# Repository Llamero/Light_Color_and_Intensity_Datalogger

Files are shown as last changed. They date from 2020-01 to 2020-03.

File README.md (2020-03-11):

# Data Logger: Temperature, Pressure, Humidity, Light Intensity and Color

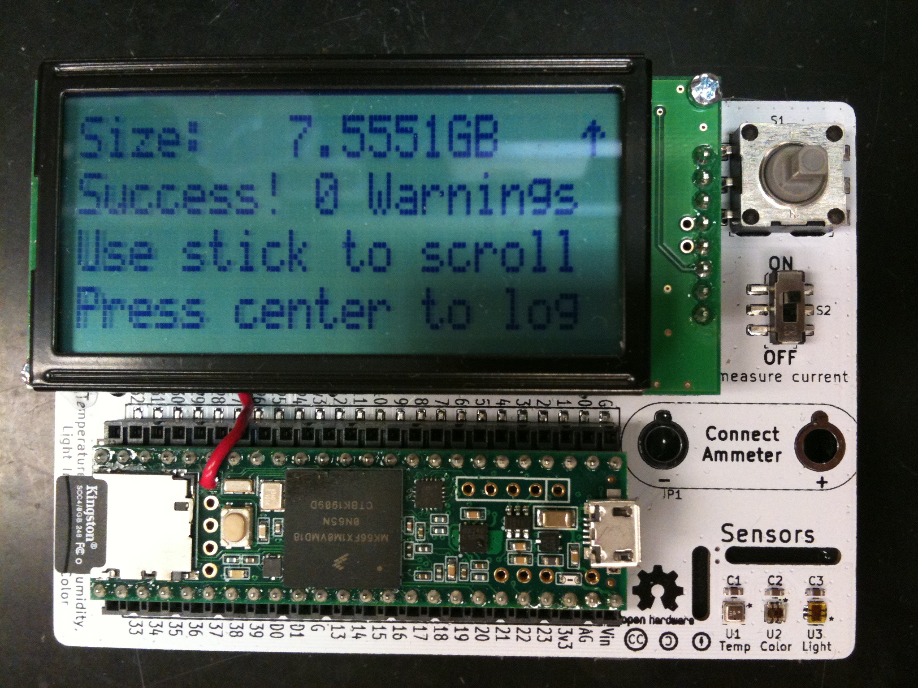
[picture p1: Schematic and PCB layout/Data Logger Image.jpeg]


## Summary:

This is an open-source data logger that can record air temperature, air pressure, relative humidity, visible light instensity, near-infrared light intensity, and visible light color (RGB).  This data logger can record at up to 1 Hz onto a FAT32 formatted SD card.  At 1Hz and with a full battery pack (6 AAs) the data logger should run for 200+ days on a single pack (depending on the SD card), with lower sampling frequencies increasing the duration to a maximum of >800 days (depending on the SD card).  The light sensors employ an autogain feature with the intensity sensor having a 600,000,000:1 dynamic range, and a minimum sensitivity at about 1.0 nW/cm2.

Windows users: Use this program to format SD cards >32 GB http://www.ridgecrop.demon.co.uk/index.htm?guiformat.htm

For information on ordering, assembly, and programming, please see the instruction manual. 

Development of this data logger was funded by NIH P30-EY003176-32

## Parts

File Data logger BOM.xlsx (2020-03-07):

Part ID | Value | Footprint | Manufacturer | Manufacturer Part # | Digikey Part # | Quantity | Link
BT1 | BU2032SM-BT-GTR | Ben_Custom:BU2032SM-BT-GTR | MPD (Memory Protection Devices) | BU2032SM-BT-GTR | BU2032SM-BT-GCT-ND | 1 | https://www.digikey.com/product-detail/en/mpd-memory-protection-devices/BU2032SM-BT-GTR/BU2032SM-BT-GCT-ND/3628531
BT2, BT3 | Battery | Ben_Custom:BH3AAW-Battery_wire_pads | MPD (Memory Protection Devices) | SBH331A | SBH331A-ND | 2 | https://www.digikey.com/products/en?keywords=SBH331A-ND
C1-C3 | 1uF | Capacitors_SMD:C_0603 | TDK Corporation | C1608X7R1C105K080AC | 445-1604-1-ND | 3 | https://www.digikey.com/products/en?keywords=445-1604-1-ND
C4 | 100uF | Capacitors_SMD:C_1206 | Samsung Electro-Mechanics | CL31A107MQHNNNE | 1276-1782-1-ND | 1 | https://www.digikey.com/products/en?keywords=1276-1782-1-ND
D1-D2 | D | Diodes_SMD:D_SOD-323 | Toshiba Semiconductor and Storage | CUS10S30,H3F | CUS10S30H3FCT-ND | 2 | https://www.digikey.com/products/en?keywords=CUS10S30H3FCT-ND
LCD1 | NHD-0420H1Z-FL-GBW-33V3 | Ben_Custom:NHD-0420H1Z-FL-GBW-33V3_Display_with_Header | Newhaven Display Intl | NHD-0420H1Z-FL-GBW-33V3 | NHD-0420H1Z-FL-GBW-33V3-ND | 1 | https://www.digikey.com/products/en?keywords=NHD-0420H1Z-FL-GBW-33V3
LCD Header | SSM-108-L-SV-BE-LC | Ben_Custom:NHD-0420H1Z-FL-GBW-33V3_Display_with_Header | Samtec Inc. | SSM-108-L-SV-BE-LC | SSM-108-L-SV-BE-LC-ND | 2 | https://www.digikey.com/products/en?keywords=SSM-108-L-SV-BE-LC-ND
LCD Standoff | 970100244 | Ben_Custom:NHD-0420H1Z-FL-GBW-33V3_Display_with_Header | Würth Elektronik | 970100244 | 732-12845-ND | 2 | https://www.digikey.com/products/en?keywords=732-12845-ND
LCD Bolt | MPMS 002 0005 PH | Ben_Custom:NHD-0420H1Z-FL-GBW-33V3_Display_with_Header | B&F Fastener Supply | MPMS 002 0005 PH | H738-ND | 100 | https://www.digikey.com/products/en/hardware-fasteners-accessories/screws-bolts/572?k=H738-ND
Q1 | Q_NMOS_GSD | TO_SOT_Packages_SMD:SOT-23 | Infineon Technologies | BSS806NH6327XTSA1 | BSS806NH6327XTSA1CT-ND | 1 | https://www.digikey.com/products/en?keywords=BSS806NH6327XTSA1CT-ND
R1 | EXB-2HV472JV_-_8x4.7k_resistor_array | Ben_Custom:4816P-1-472LF | Bourns Inc. | 4816P-1-472LF | 4816P-1-472LFCT-ND | 1 | https://www.digikey.com/products/en?keywords=4816P-1-472LFCT-ND
R2 | 2 Ohm | Resistors_SMD:R_0603 | Yageo | RC0603FR-072RL | 311-2.00HRCT-ND | 1 | https://www.digikey.com/products/en?keywords=311-2.00HRCT-ND
S1 | JS5208 | digikey-footprints:Switch_Nav_12.4x12.4mm_SMD_JS5208 | E-Switch | JS5208 | EG4561-ND | 1 | https://www.digikey.com/products/en?keywords=EG4561-ND
S2 | JS202011SCQN | digikey-footprints:Switch_Slide_JS202011SCQN | C&K | JS202011SCQN | 401-2002-1-ND | 1 | https://www.digikey.com/products/en?keywords=401-2002-1-ND
U1 | BME280 | digikey-footprints:Pressure_Sensor_LGA-8_2.5x2.5mm_BME280 | Bosch Sensortec | BME280 | 828-1063-1-ND | 1 | https://www.digikey.com/products/en?keywords=828-1063-1-ND
U2 | TCS34725FN | Ben_Custom:TCS34725 | ams | TCS34725FN | TCS34725FNCT-ND | 1 | https://www.digikey.com/products/en?keywords=TCS34725FNCT-ND
U3 | TSL25911FN | Ben_Custom:TSL25911FN | ams | TSL25911FN | TSL25911FNCT-ND | 1 | https://www.digikey.com/products/en?keywords=TSL25911FNCT-ND
U4 | Teensy3.6 | Ben_Custom:Teensy3.6_doublewide_header | SparkFun Electronics | DEV-14058 | 1568-1465-ND | 1 | https://www.digikey.com/products/en?keywords=1568-1465-ND
U5 | TS12A4514DBVR | TO_SOT_Packages_SMD:SOT-23-5 |  | TS12A4514DBVR | 296-24201-1-ND | 1 | https://www.digikey.com/products/en?keywords=296-24201-1-ND
Teensy Header | SSM-124-L-DV-LC | Ben_Custom:Teensy3.6_doublewide_header | Samtec Inc. | SSM-124-L-DV-LC | SSM-124-L-DV-LC-ND | 2 | https://www.digikey.com/products/en?keywords=SSM-124-L-DV-LC-ND
# of decives: | 1

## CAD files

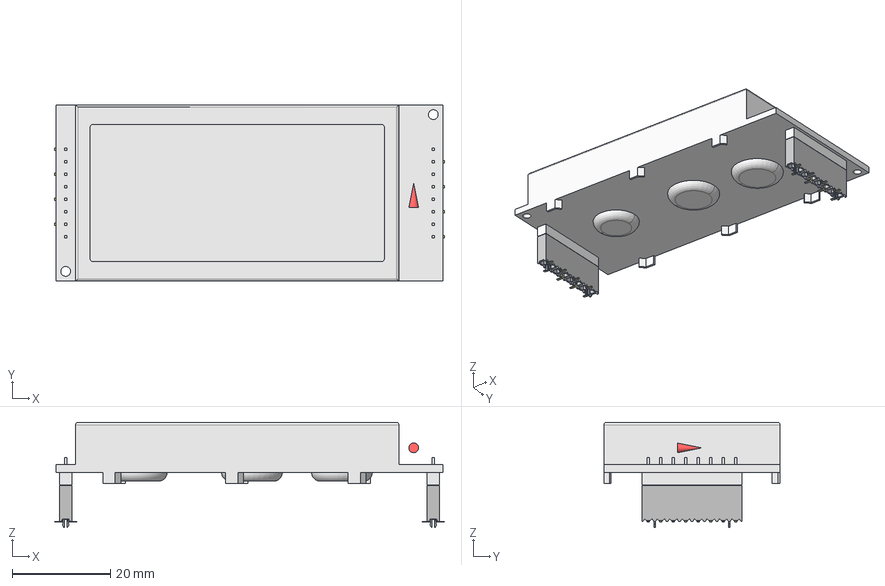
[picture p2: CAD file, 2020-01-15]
Schematic and PCB layout/Light_intensity_data_logger/CAD files/Display with header.FCStd
79.6 x 36.0 x 21.5 mm
NHD_0420H1Z
_SSM-108-L-SV-BE-LC_body
_C-95-028
_SSM-108-L-SV-BE-LC_body001
_C-95-029

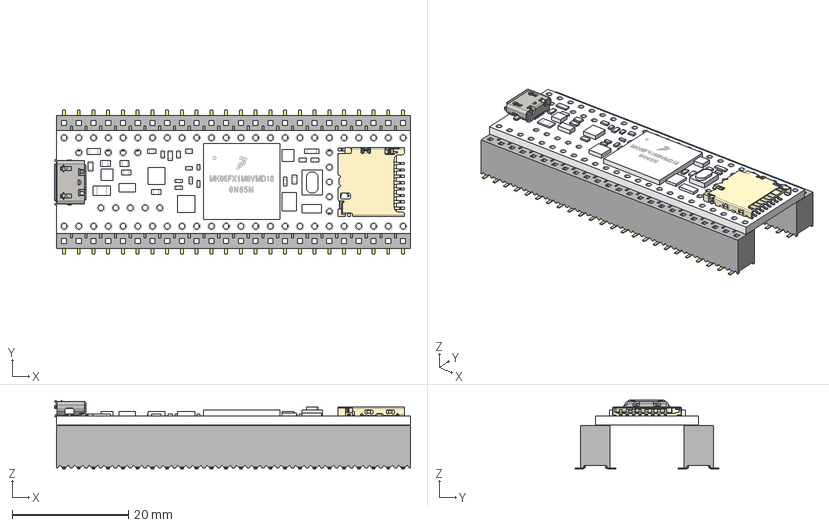
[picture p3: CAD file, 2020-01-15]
Schematic and PCB layout/Light_intensity_data_logger/CAD files/Teensy 35_36 on doublewide header.FCStd
61.3 x 24.8 x 11.8 mm
Teensy 3_5
DM3D-SF
_SSM-124-T-DV_body
_C-137-0124
_SSM-124-T-DV_body001
_C-137-0125

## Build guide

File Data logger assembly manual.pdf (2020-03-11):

# Data logger Manual

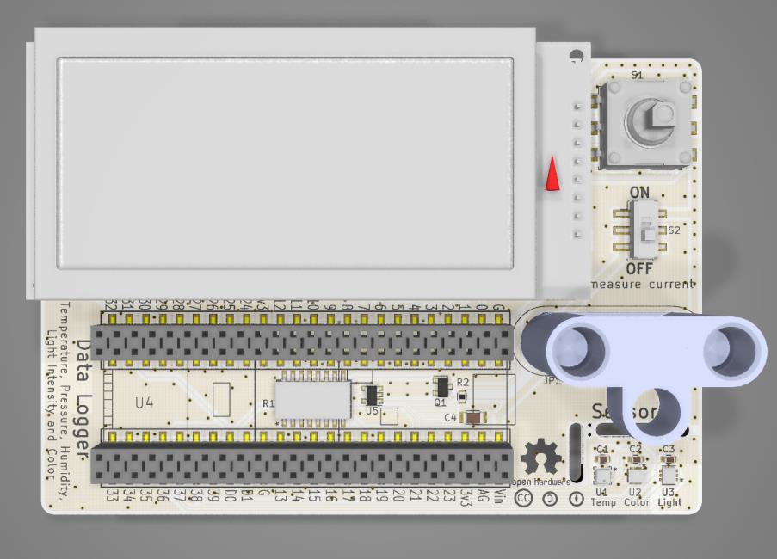
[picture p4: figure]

# Board ordering

To build the data logger, you will need a PCB board. To greatly ease assembly, you will also want a solder paste stencil. Both of these can be easily ordered by submitting the Gerber files to a PCB and stencil fabricator. Several such vendors include Aisler, PCBWay, JLCPCB, etc.

Board specifications:

Size: 69 x 100 mm

Board: 1.6 mm FR4

Copper : 1 oz/ft²

Surface finish: HASL with lead or ENIG

Vias: Tented

Stencil specifications:

Type: Non-framework (unless you have a stencil printer: http://www.madelltech.com/m2-4.html)

Electropolishing: Yes (this is essential to prevent the solder paste from sticking onto the stencil)

# Parts ordering

Parts can be easily ordered by submitting the bill-of-materials (Data logger BOM.xlsx) (https://github.com/Llamero/Light_Color_and_Intensity_Datalogger/blob/master/Data%20logger%20BOM.xlsx) to any major parts vendor including Digikey (https://www.digikey.com/bom) or Mouser (https://www.mouser.com/bom/). The BOM is setup to automatically calculate the number of parts needed based on the number of boards specified.

# Equipment needed:

Tape

Single edge razor blade

Disposable stirrer (pipette tips work well)

Soldering iron

Solder

Solder paste

Solder flux

Magnifying glass or microscope

Tweezers or forceps

Thermometer

Hot plate

Hot glue gun

Aluminum foil

Disposable latex or nitrile gloves

70% Ethanol or rubbing alcohol

Optional: Container for pre-sorting components

# Soldering the board

Before starting with assembly of the board be sure to read and understand all of the following instructions. Once the solder paste is applied the board must be reflowed within two hours or too much of the flux will evaporate. Also be sure to change your gloves regularly during the application of the solder paste. Solder paste can readily get into the skin, posing a health hazard. Hazards aside, assembling a PCB board is very much akin to building a model or advanced Lego® kit with no advanced skills required. Here is an additional tutorial on solder paste stenciling (https://www.sparkfun.com/tutorials/58) and reflow (https://www.sparkfun.com/tutorials/59).

### Step 1: Tape PCB boards together

You want to tape the board to another PCB board so that the stencil can be attached to a flat surface.

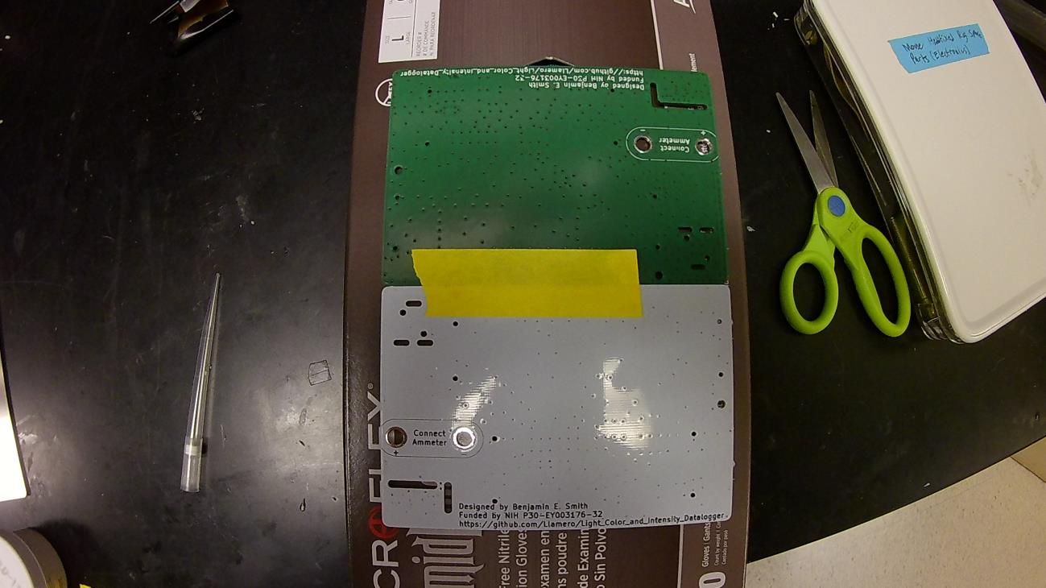
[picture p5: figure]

### Step 2: Align stencil onto PCB

Using a microscope or magnifying glass, try to align the stencil as accurately as possible with all of the stencil holes lining up with all of the PCB pads. Small errors (less than half a pad spacing) are tolerable as the solder will wick to the correct position, but the more aligned the better. The sensor pads are the most closely spaced, so be extra careful to align them properly.

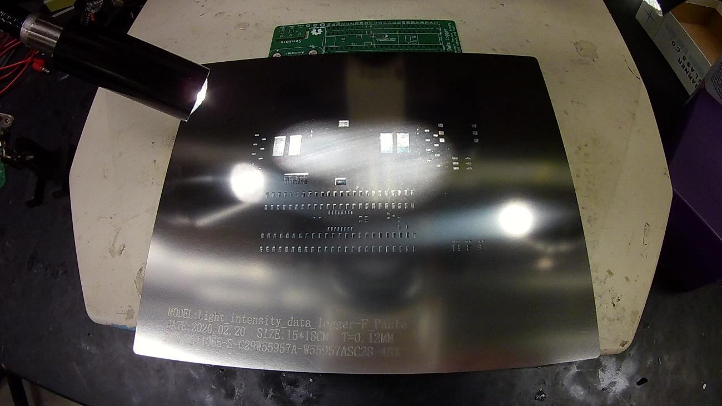
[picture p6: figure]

### Step 3: Tape stencil in place onto spare PCB

Carefully tape the stencil into place, and then press down the on the stencil to check the alignment. Repeat steps 2-3 if the stencil looks off center.

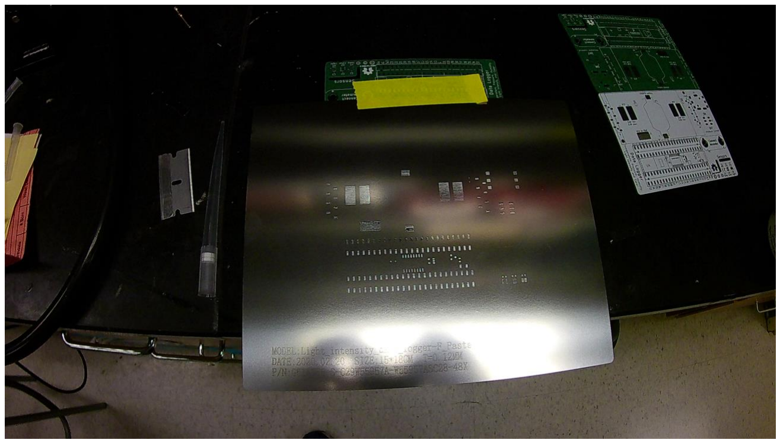
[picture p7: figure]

### Step 4: Thoroughly mix the solder paste

Put on a pair of disposable gloves and vigorously mix the solder paste with a disposable stirrer (such as a pipette tip) for at least one minute. Inadequately mixed solder paste can lead to poor solder reflow.

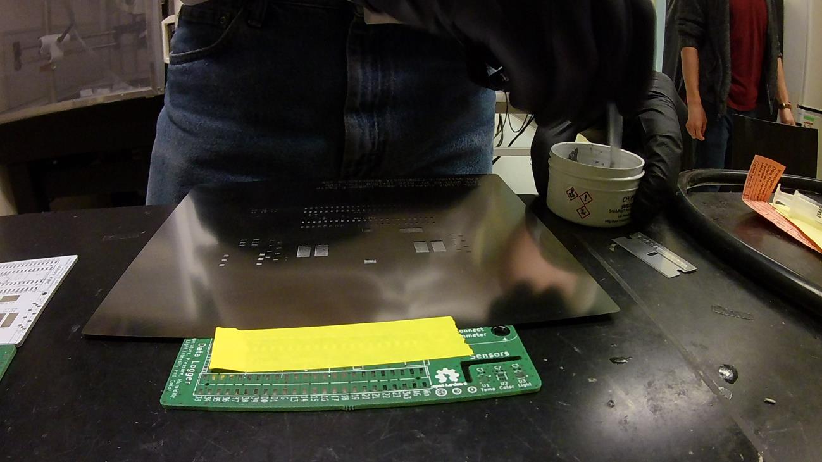
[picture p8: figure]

### Step 5: Apply solder paste to the razor blade

Using the stirrer to apply a generous amount of solder paste to the blade edge of the razor blade.

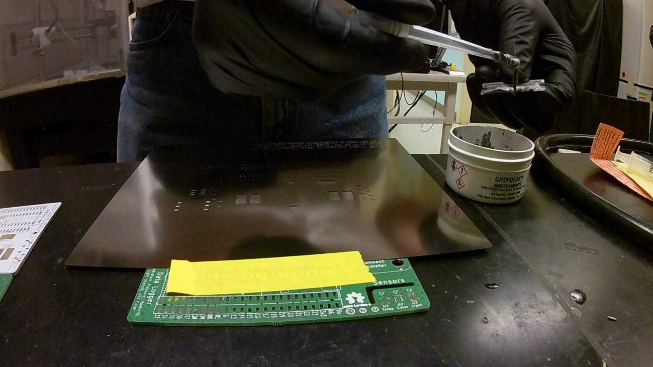
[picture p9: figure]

### Step 6: Apply thick layer of solder paste to the stencil

Use the razor blade to apply a coat of solder paste to the stencil, ensuring you cover all of the pads. Try to move across the stencil at a 45° angle to reduce the risk of pressing paste under the stencil. It will likely take multiple applications to cover the entire stencil.

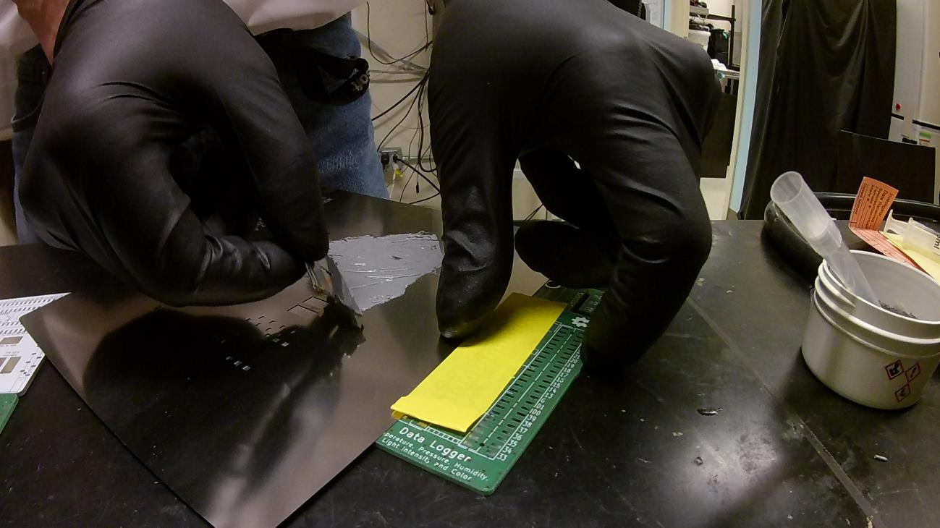
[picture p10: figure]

### Step 7: Remove all excess solder paste

Press the razor blade onto the stencil and carefully scrape off all of the excess solder paste. Use the stirrer to remove the excess paste from the blade and return it to the solder paste container.

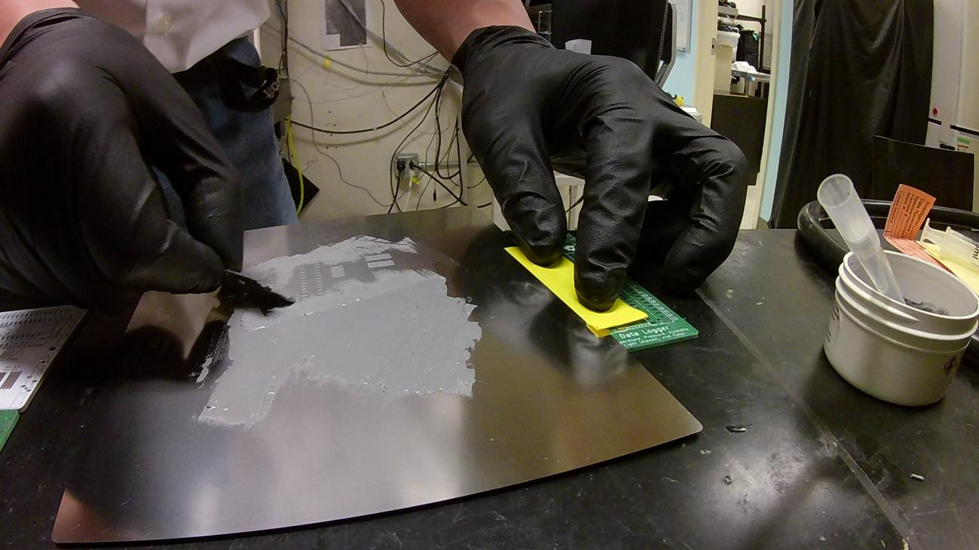
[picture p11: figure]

### Step 8: Lift the stencil from the PCB board

Once all of the excess paste is removed from the stencil, lift the stencil from the PCB by pulling up on the side opposite the tape. Once the stencil is clear of the PCB, carefully remove the tape from the stencil and PCB, and remove the spare PCB the stencil was attached to. Inspect the PCB to make sure all the pads are covered in solder paste, and then properly dispose of the blade and stirrer, and clean the stencil thoroughly with 70% ethanol or rubbing alcohol. Also return the solder paste to 4°C storage.

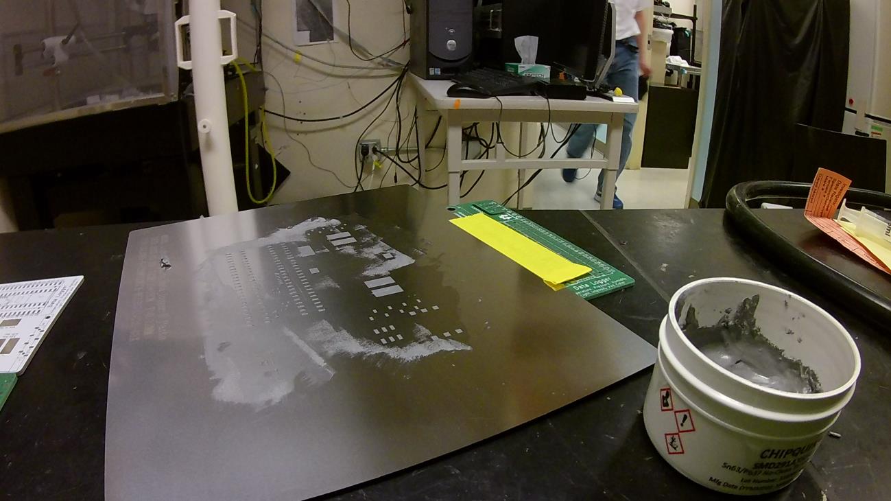
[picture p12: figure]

### Step 9: Add components to the PCB board

Using forceps, carefully place each component onto the board. All components should have a numerical identifier on the BOM (such as “R1”) that corresponds to a marking on the board. Chips that have a specific orientation will have a dot next to pin #1, and there is as asterisk next to the corresponding pad on the PCB. Diodes should be aligned such that the line on the diode goes into the U shaped mark on the PCB: The light sensors are an exception since the epoxy cover is clear. For these chips, pin #1 is marked by a pad that is thinner than the other pads (see picture below – the green arrow points to the pin #1 pad which is thinner than the other three corner pads – magenta arrows). Do not add the joystick (S1) as this will be hand soldered on later.

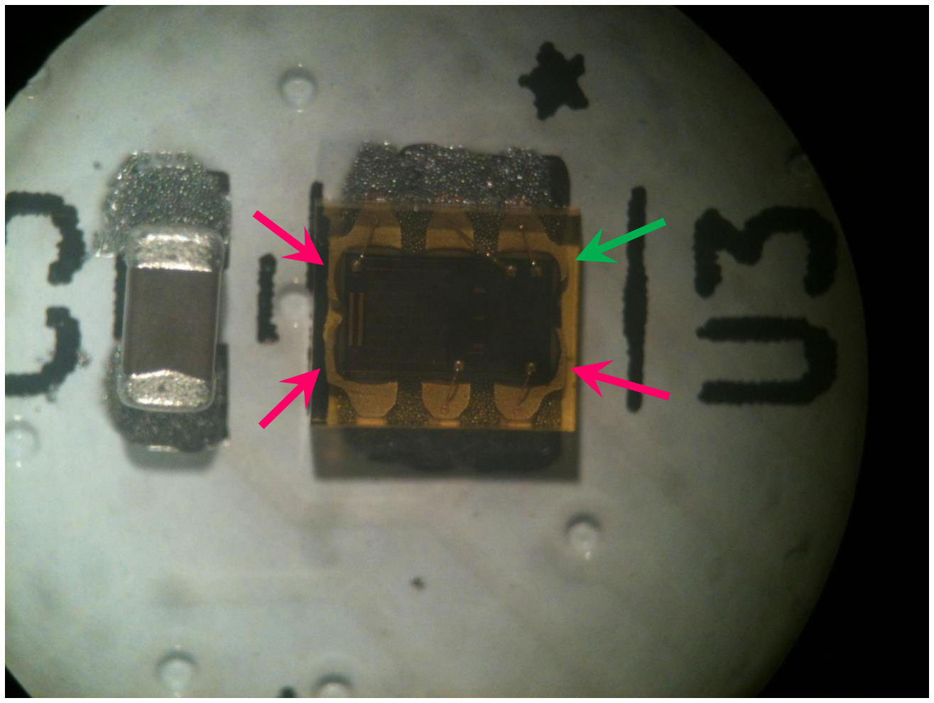
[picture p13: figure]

### Step 10: Reflow the board

Once all of the parts are placed, double check all the components to make sure they are oriented properly, then transfer the board onto a piece of aluminum foil, and place the boards onto a hot plate. Make sure the hot plate is near a fume hood or is in a well ventilated area, as the flux will fume as it burns off. Turn on the heat to the hot plate and monitor the temperature with the thermometer. If you are using lead solder paste, the solder should melt at 183°C. Continue heating the board to around 220°C, and make sure that all of the solder has melted. Since the solder is under the sensors, you can gently tap the sensor chips with a pair of forceps. If they snap back, the solder has melted. Carefully lift the aluminum foil with the boards off of the hot plate, and allow them to cool.

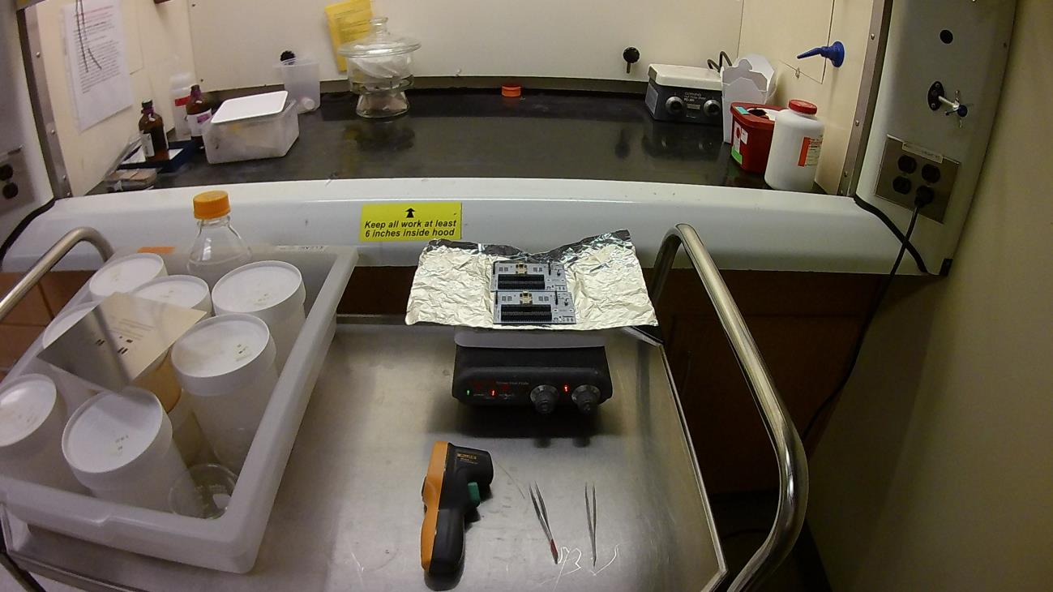
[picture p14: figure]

### Step 11: Inspect the board

Once the boards have cooled, inspect all of the solder joints to make sure they reflowed properly. All joints should look shiny. If you see dull joints, these have not fully reflowed, so apply a small amount of flux to the joint and melt it with a soldering iron. Solder bridges (two or more pins soldered together) can be easily removed by applying a small amount of flux to the bridge, and then tapping the bridge with a clean soldering iron.

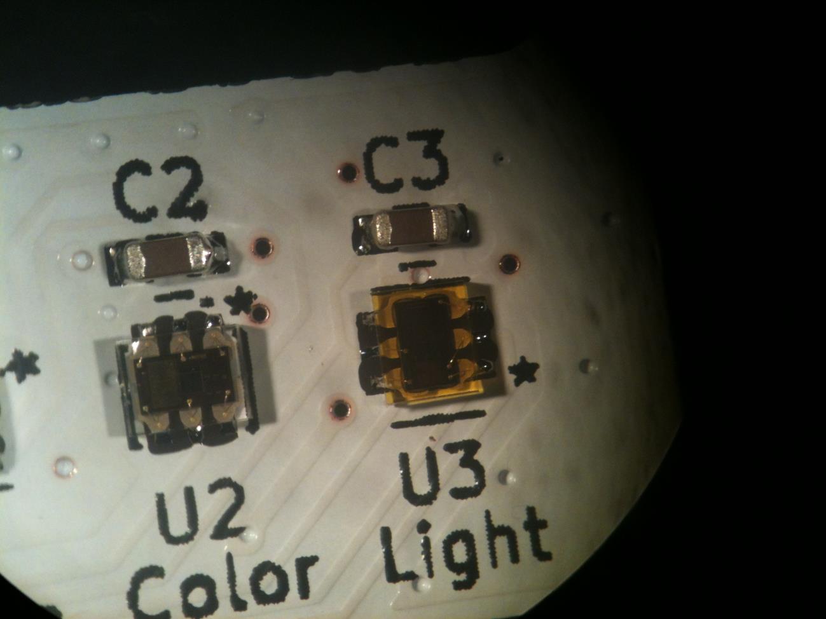
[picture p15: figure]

### Step 12: Solder the joystick onto the board and drill the battery pack

Place the joystick into its corresponding slot on the board, and hand solder each pin to the board. You can also add the CR2032 battery at this time. Optional: If you want to use banana clips to test the data logger current usage, place the battery pack under the board, and trace the two banana clip through holes onto the battery pack. Then drill the corresponding holes ( >4.5 mm in diameter) into the battery pack.

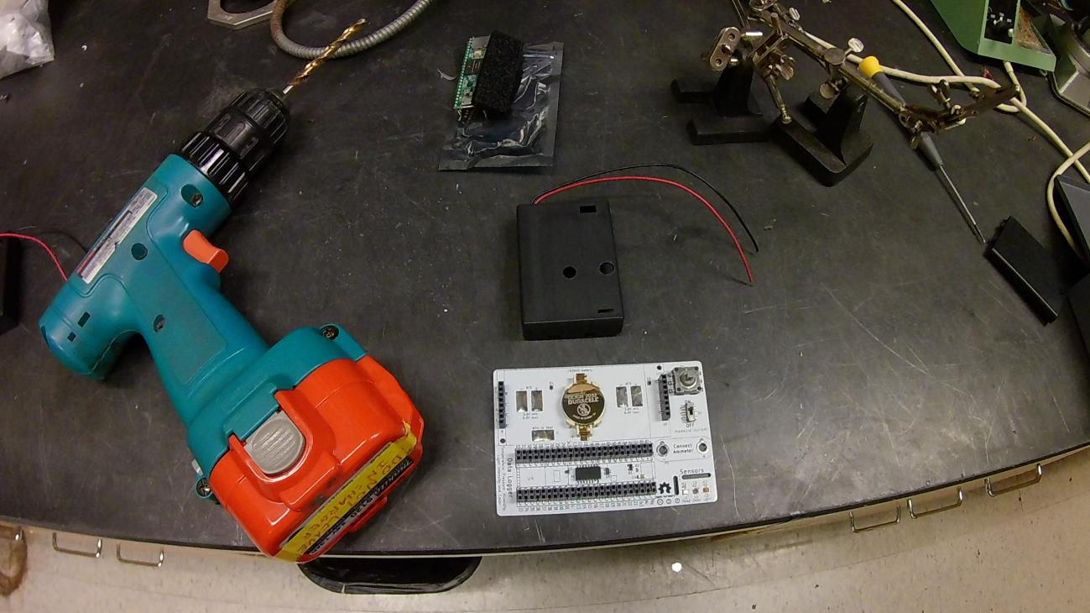
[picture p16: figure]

### Step 13: Connect the real-time clock battery to the Teensy

Cut a piece of wire from one of the battery pack leads, and solder the wire to the through-hole marked “Vbat” on the Teensy. Insert the Teensy into the headers and then solder the other end of the wire to the pad marked “Wire to Vbat”.

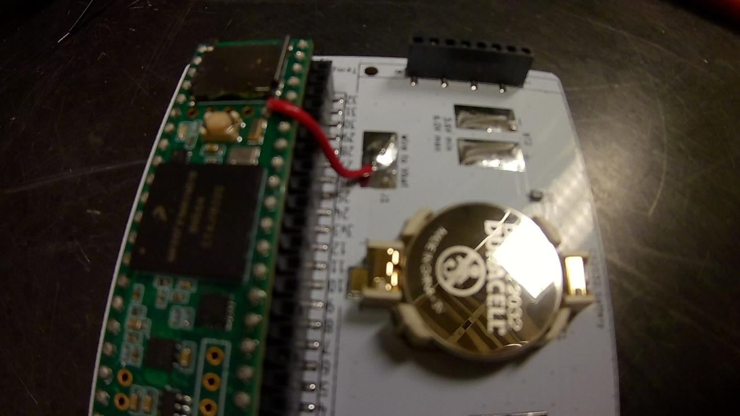
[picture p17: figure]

### Step 14: Glue the battery packs to the data logger

Using hot glue, trace a line of glue around the battery pack, and press it onto the PCB board. For a stronger joint, you can pre-heat the PCB board and battery pack with a hot air gun.

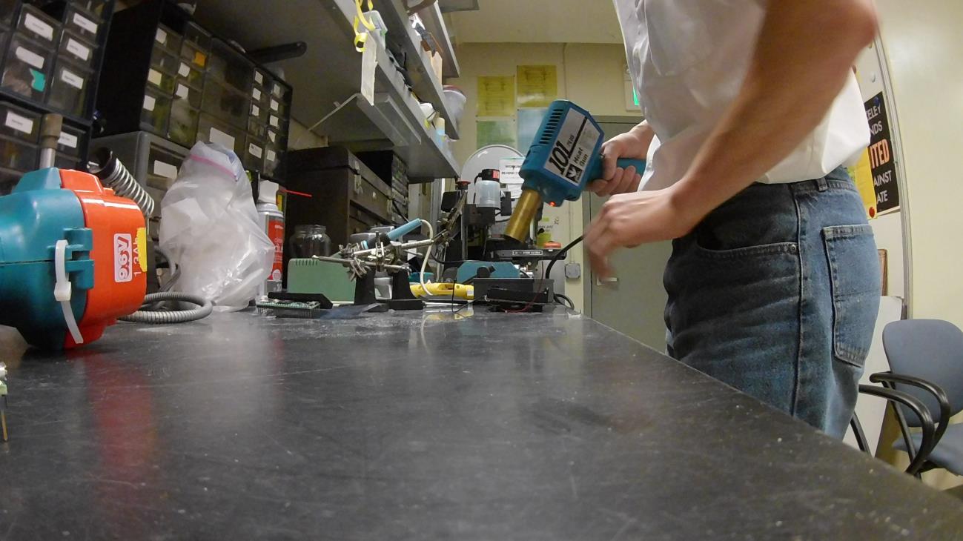
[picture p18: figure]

### Step 15: Solder battery packs to the PCB board and glue on standoffs

Cut the wire leads to length, and solder the wire leads to the PCB board with the red wire going to the “+” pad and the black wire going to the “-“ pad. Then bolt the standoffs to the LCD screen, apply glue to the base of the standoffs, and insert the screen into the headers. For a more secure bond, then heat the standoffs with a hot air gun to heat the standoff and board and remelt the glue.

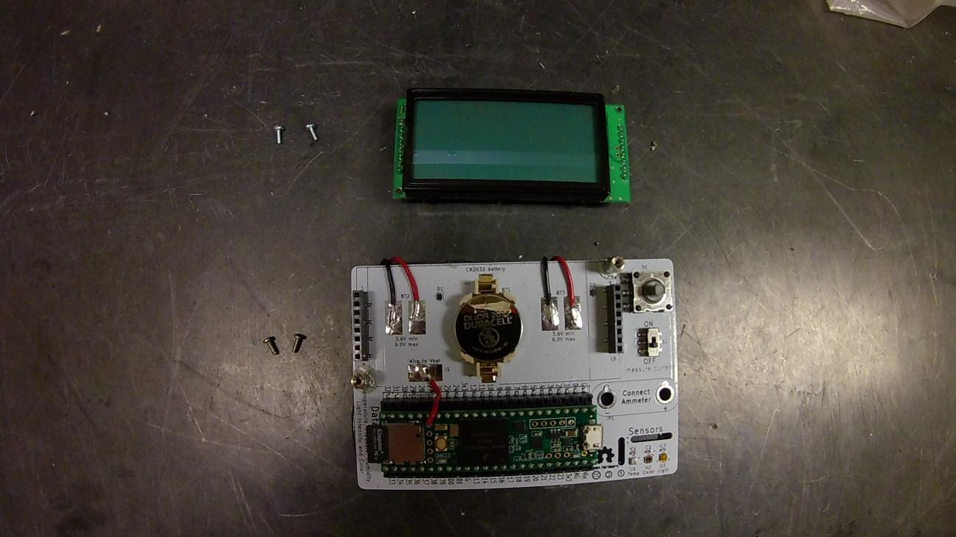
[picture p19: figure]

### Step 16: Finish assembly

Add 3 AA batteries to each battery pack and close the lid on the pack, and use the supplied bolt to lock the lid in place.

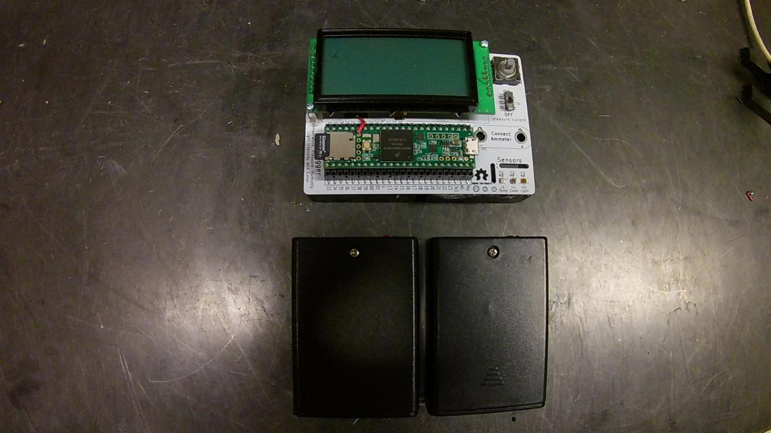
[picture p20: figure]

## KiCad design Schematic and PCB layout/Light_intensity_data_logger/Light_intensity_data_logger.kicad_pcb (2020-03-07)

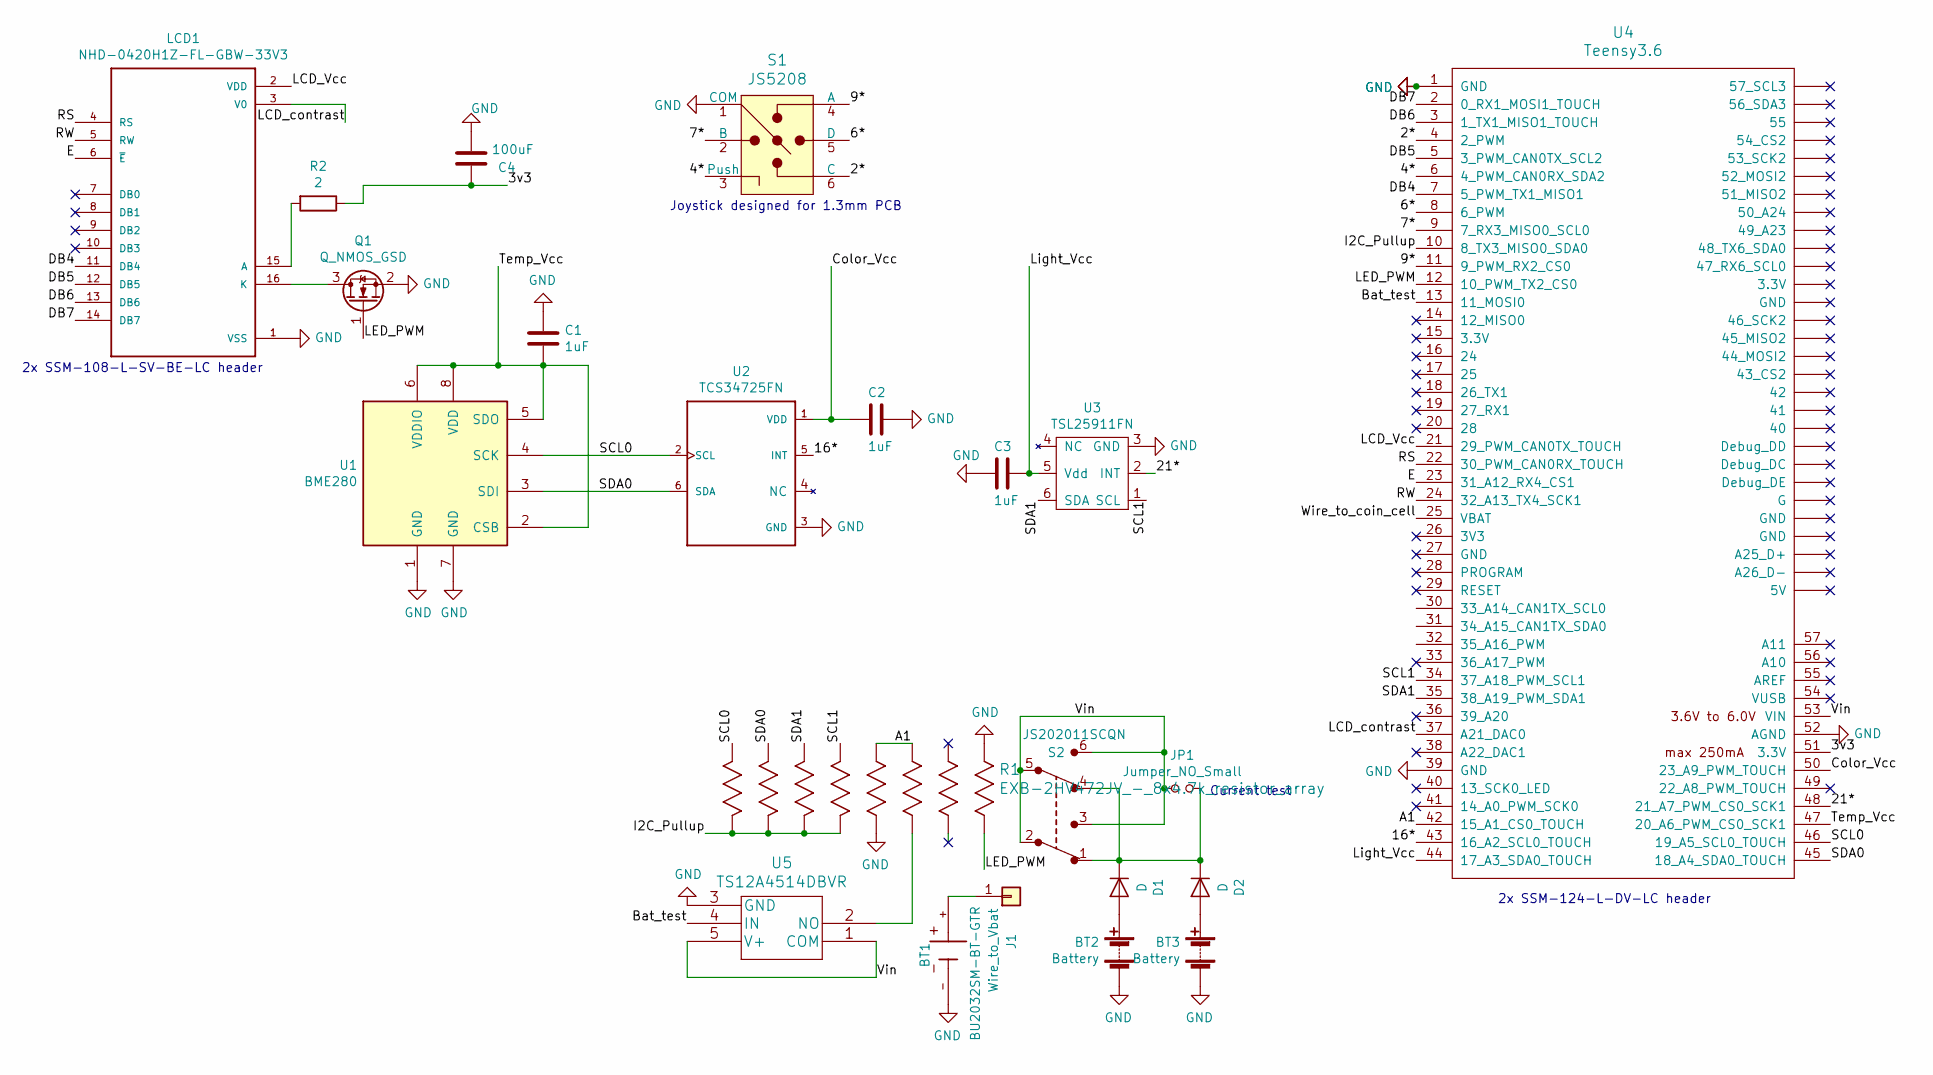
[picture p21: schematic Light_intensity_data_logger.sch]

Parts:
BT1: BU2032SM-BT-GTR; Part# BU2032SM-BT-GCT-ND
BT2, BT3: Battery; BH3AAW-Battery_wire_pads; Part# SBH331A-ND
C1, C2, C3: 1uF; C_0603; Part# 445-1604-1-ND
C4: 100uF; C_1206; Part# 1276-1782-1-ND
D1, D2: D; D_SOD-323; Part# CUS10S30H3FCT-ND
J1: Wire_to_Vbat; SolderWirePad_single_SMD_5x10mm
JP1: Jumper_NO_Small; Banana_Jack_2Pin
LCD1: NHD-0420H1Z-FL-GBW-33V3; NHD-0420H1Z-FL-GBW-33V3_Display_with_Header; Part# NHD-0420H1Z-FL-GBW-33V3
Q1: Q_NMOS_GSD; SOT-23; Part# BSS806NH6327XTSA1CT-ND
R1: EXB-2HV472JV_-_8x4.7k_resistor_array; 4816P-1-472LF; Part# 4816P-1-472LFCT-ND
R2: 2; R_0603; Part# 311-2.00HRCT-ND
S1: JS5208; Switch_Nav_12.4x12.4mm_SMD_JS5208; Part# EG4561-ND
S2: JS202011SCQN; Switch_Slide_JS202011SCQN; Part# 401-2002-1-ND
U1: BME280; Pressure_Sensor_LGA-8_2.5x2.5mm_BME280; Part# 828-1063-1-ND
U2: TCS34725FN; TCS34725; Part# TCS34725FNCT-ND
U3: TSL25911FN; Part# TSL25911FNCT-ND
U4: Teensy3.6; Teensy3.6_doublewide_header; Part# 1568-1465-ND
U5: TS12A4514DBVR; SOT-23-5

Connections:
/2*: S1.6 (C), U4.4 (2_PWM)
/3v3: C4.1, R2.1, U4.51 (3.3V)
/4*: S1.3 (Push), U4.6 (4_PWM_CAN0RX_SDA2)
/6*: S1.5 (D), U4.8 (6_PWM)
/7*: S1.2 (B), U4.9 (7_RX3_MISO0_SCL0)
/9*: S1.4 (A), U4.11 (9_PWM_RX2_CS0)
/16*: U2.5 (INT), U4.43 (16_A2_SCL0_TOUCH)
/21*: U3.2 (INT), U4.48 (21_A7_PWM_CS0_SCK1)
/A1: R1.3, R1.4, U4.42 (15_A1_CS0_TOUCH)
/Bat_test: U4.13 (11_MOSI0), U5.4 (IN)
/Color_Vcc: C2.2, U2.1 (VDD), U4.50 (23_A9_PWM_TOUCH)
/DB4: LCD1.11 (DB4), U4.7 (5_PWM_TX1_MISO1)
/DB5: LCD1.12 (DB5), U4.5 (3_PWM_CAN0TX_SCL2)
/DB6: LCD1.13 (DB6), U4.3 (1_TX1_MISO1_TOUCH)
/DB7: LCD1.14 (DB7), U4.2 (0_RX1_MOSI1_TOUCH)
/E: LCD1.6 (~E~), U4.23 (31_A12_RX4_CS1)
/I2C_Pullup: R1.9, R1.10, R1.11, R1.12, U4.10 (8_TX3_MISO0_SDA0)
/LCD_Vcc: LCD1.2 (VDD), U4.21 (29_PWM_CAN0TX_TOUCH)
/LCD_contrast: LCD1.3 (V0), U4.37 (A21_DAC0)
/LED_PWM: Q1.1 (G), R1.16, U4.12 (10_PWM_TX2_CS0)
/Light_Vcc: C3.1, U3.5 (Vdd), U4.44 (17_A3_SDA0_TOUCH)
/RS: LCD1.4 (RS), U4.22 (30_PWM_CAN0RX_TOUCH)
/RW: LCD1.5 (RW), U4.24 (32_A13_TX4_SCK1)
/SCL0: R1.8, U1.4 (SCK), U2.2 (SCL), U4.46 (19_A5_SCL0_TOUCH)
/SCL1: R1.5, U3.1 (SCL), U4.34 (37_A18_PWM_SCL1)
/SDA0: R1.7, U1.3 (SDI), U2.6 (SDA), U4.45 (18_A4_SDA0_TOUCH)
/SDA1: R1.6, U3.6 (SDA), U4.35 (38_A19_PWM_SDA1)
/Temp_Vcc: C1.2, U1.2 (CSB), U1.5 (SDO), U1.6 (VDDIO), U1.8 (VDD), U4.47 (20_A6_PWM_CS0_SCK1)
/Vin: JP1.1, S2.2, S2.3, S2.5, S2.6, U4.53 (VIN), U5.1 (COM), U5.5 (V+)
GND: BT1.-, BT2.2 (-), BT3.2 (-), C1.1, C2.1, C3.2, C4.2, LCD1.1 (VSS), Q1.2 (S), R1.1, R1.13, S1.1 (COM), U1.1 (GND), U1.7 (GND), U2.3 (GND), U3.3 (GND), U4.1 (GND), U4.39 (GND), U4.52 (AGND), U5.3 (GND)
unnamed: BT1.+, J1.1
unnamed: BT2.1 (+), D1.2 (A)
unnamed: BT3.1 (+), D2.2 (A)
unnamed: D1.1 (K), D2.1 (K), JP1.2, S2.1, S2.4
unnamed: LCD1.15 (A), R2.2
unnamed: LCD1.16 (K), Q1.3 (D)
unnamed: R1.14, U5.2 (NO)

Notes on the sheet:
Current test
Joystick designed for 1.3mm PCB
2x SSM-108-L-SV-BE-LC header
2x SSM-124-L-DV-LC header

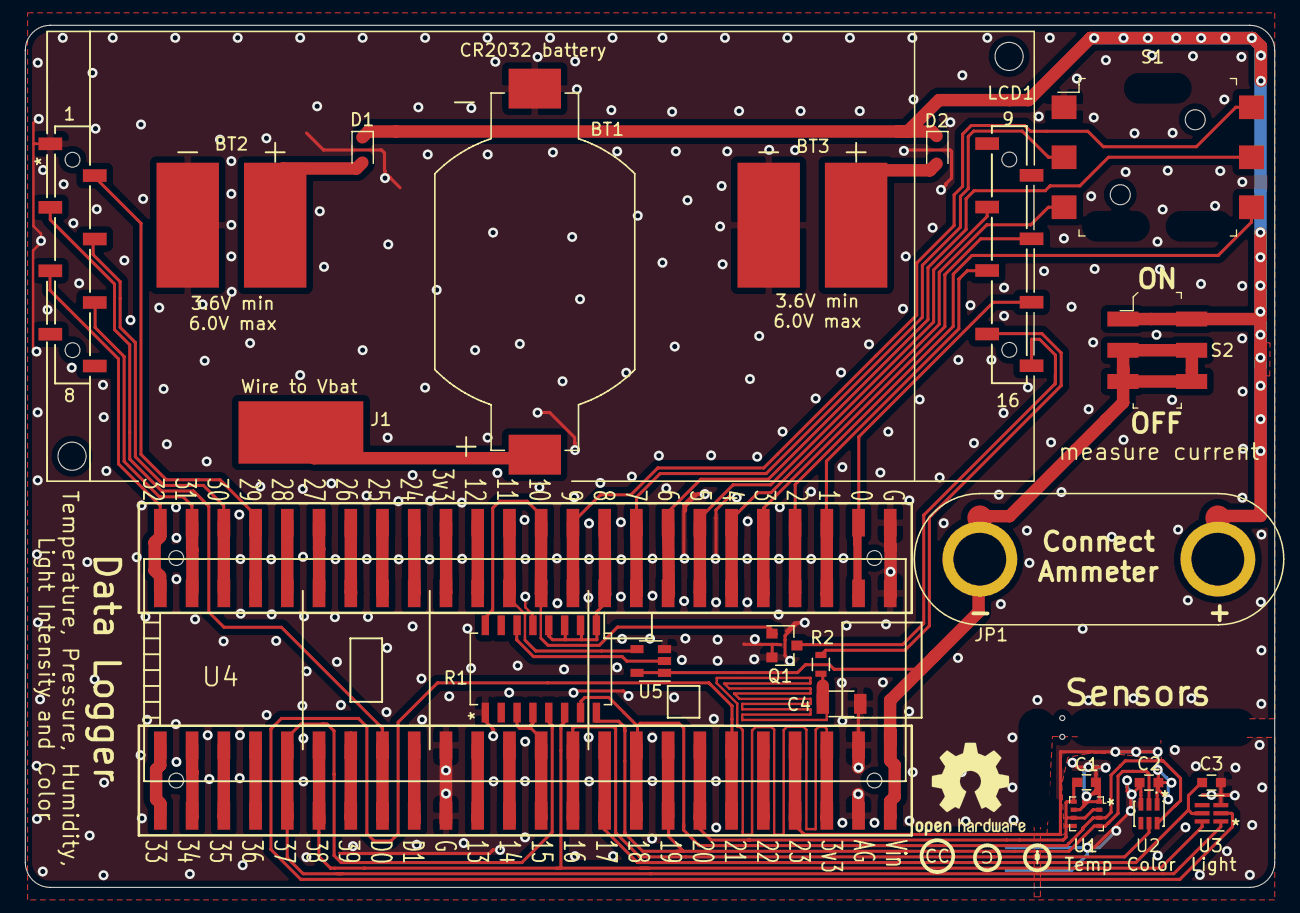
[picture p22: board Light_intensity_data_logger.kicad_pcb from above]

Board: 2 copper layers, 100.0 x 69.0 mm, 22 parts (0 on the bottom side), 37 nets.

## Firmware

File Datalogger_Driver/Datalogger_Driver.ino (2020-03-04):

#include "Adafruit_BME280.h" //Temp, pressure, humidity sensor
#include "Adafruit_Sensor.h" //Universal sensor API
#include "Adafruit_TCS34725.h" //Color Sensor
#include "Adafruit_TSL2591.h" //Light Sensor
#include "LiquidCrystalFast.h" //Display
#include <Wire.h> //I2C
#include <TimeLib.h> //Set RTC time and get time strings
#include <Snooze.h> //Put Teensy into low power state between log points
#include <SD.h> //Store data onto SD card
#include <ADC.h>


//Define software restart
#define RESTART_ADDR       0xE000ED0C
#define READ_RESTART()     (*(volatile uint32_t *)RESTART_ADDR)
#define WRITE_RESTART(val) ((*(volatile uint32_t *)RESTART_ADDR) = (val))

//Setup default parameters
uint8_t log_interval_array[] = {0, 0, 10}; //Number of hours, minutes, and seconds between log intervals
const char boot_dir[] = "boot_log"; //Directory to save boot log files into - max length 8 char
const char log_dir[] = "data_log"; //Directory to save data log files into - max length 8 char
boolean measure_temp = true;
boolean measure_humidity = true;
boolean measure_pressure = true;
boolean measure_lux = true;
boolean measure_color = true;
boolean measure_Vin = true;

boolean disable_display_on_log = true; //Completely power down display during logging
boolean save_on_log_interval = false; //Save to SD every log interval - this is less battery efficient during saves than saving in 512 byte blocks, but will ensure no loss of data 
const float default_backlight = 0; //Set default backlight intensity to full brightness (range is 0-1)
const float default_contrast = 0.7; //Set default LCD contrast to half range (range is 0-1)

//Allow Teensy to re-run setup when settings are changed - Call "CPU_RESTART"
#define CPU_RESTART_ADDR (uint32_t *)0xE000ED0C
#define CPU_RESTART_VAL 0x5FA0004
#define CPU_RESTART (*CPU_RESTART_ADDR = CPU_RESTART_VAL);

// Load drivers
SnoozeDigital digital;
SnoozeTimer timer;
SnoozeBlock hibernate_config(digital, timer);
time_t unix_t = 0; //Track current device time
uint16_t unix_ms = 0; //Current time in ms
time_t next_log_time = 0; //next log time in unix time
time_t time_remaining = 0; //Time remaing to next log interval
time_t log_interval = (60*60*log_interval_array[0])+(60*log_interval_array[1])+log_interval_array[2];
const uint16_t log_offset = 1000; //Time in ms it takes to log a data point - also determines smallest log interval - can't be >5535 ms.
boolean log_next_wake = false; //Whether to log on the next timer wake event

//Setup LCD pin numbers and initial parameters
const uint8_t LCD_pin[] = {30, 32, 31, 5, 3, 1, 0}; //Only 4-pin supported in LiquidCrystalFast
              // LCD pins: RS  RW  EN  D4 D5 D6 D7
LiquidCrystalFast lcd(LCD_pin[0], LCD_pin[1], LCD_pin[2], LCD_pin[3], LCD_pin[4], LCD_pin[5], LCD_pin[6]);
const uint8_t LCD_toggle_pin = 29; //Set to high to power on LCD
const uint8_t LED_PWM_pin = 10; //Drive LED backlight intensity
const uint8_t contrast_pin = A21; //DAC pin for addjusting diplay contrast
const uint8_t analog_resolution = 16; //Number of bits in PWM and DAC analog  - PWM cap is 16, DAC cap is 12 - auto capped in code - https://www.pjrc.com/teensy/td_pulse.html
const uint16_t analog_max = (1<<analog_resolution)-1; //Highest analog value
const uint32_t analog_freq = 1000; //PWM frequency in Hz
ADC *adc = new ADC(); // adc object;

//Define LCD custom characters - from https://www.instructables.com/id/Custom-Large-Font-For-16x2-LCDs/
const uint8_t up_arrow[8] = {
  0b00000,
  0b00100,
  0b01110,
  0b10101,
  0b00100,
  0b00100,
  0b00100,
  0b00000
};

const uint8_t down_arrow[8] = {
  0b00000,
  0b00100,
  0b00100,
  0b00100,
  0b10101,
  0b01110,
  0b00100,
  0b00000
};


const uint8_t  gBigFontShapeTable[]  = {
//* LT[8] =
  B00111,
  B01111,
  B11111,
  B11111,
  B11111,
  B11111,
  B11111,
  B11111,
//* UB[8] =
  B11111,
  B11111,
  B11111,
  B00000,
  B00000,
  B00000,
  B00000,
  B00000,
//* RT[8] =
  B11100,
  B11110,
  B11111,
  B11111,
  B11111,
  B11111,
  B11111,
  B11111,
//* LL[8] =
  B11111,
  B11111,
  B11111,
  B11111,
  B11111,
  B11111,
  B01111,
  B00111,
//* LB[8] =
  B00000,
  B00000,
  B00000,
  B00000,
  B00000,
  B11111,
  B11111,
  B11111,
//* LR[8] =
  B11111,
  B11111,
  B11111,
  B11111,
  B11111,
  B11111,
  B11110,
  B11100,
//* UMB[8] =
  B11111,
  B11111,
  B11111,
  B00000,
  B00000,
  B00000,
  B11111,
  B11111,
//* LMB[8] =
  B11111,
  B00000,
  B00000,
  B00000,
  B00000,
  B11111,
  B11111,
  B11111


};


//************************************************************************
//* 6 numbers for each character
//* 9 means BLANK
const uint8_t gBigFontAsciiTable[]  = {

  32, 32, 32, 32, 32, 32,   //  0x20  space
  32, 0,  32, 32, 4,  32,   //  0x21  !
  32, 32, 32, 32, 32, 32,   //  0x22
  32, 32, 32, 32, 32, 32,   //  0x23
  32, 32, 32, 32, 32, 32,   //  0x24
  32, 32, 32, 32, 32, 32,   //  0x25
  32, 32, 32, 32, 32, 32,   //  0x26
  32, 32, 32, 32, 32, 32,   //  0x27
  32, 32, 32, 32, 32, 32,   //  0x28
  32, 32, 32, 32, 32, 32,   //  0x29
  32, 32, 32, 32, 32, 32,   //  0x2A
  32, 32, 32, 32, 32, 32,   //  0x2B
  32, 32, 32, 32, 32, 32,   //  0x2C
  32, 32, 32, 32, 32, 32,   //  0x2D
  32, 32, 32, 32, 4,  32,   //  0x2E  . (period)
  32, 32, 32, 32, 32, 32,   //  0x2F


  0,  1,  2,  3,  4,  5,    //  0x30  0
  1,  2,  32, 32, 5,  32,   //  0x31  1
  6,  6,  2,  3,  7,  7,    //  0x32  2
  6,  6,  2,  7,  7,  5,    //  0x33  3
  3,  4,  2,  32, 32, 5,    //  0x34  4
  255,6,  6,  7,  7,  5,    //  0x35  5
//  0,  6,  6,  7,  7,  5,    //  0x35  5
  0,  6,  6,  3,  7,  5,    //  0x36  6
  1,  1,  2,  32, 0,  32,   //  0x37  7
  0,  6,  2,  3,  7,  5,    //  0x38  8
  0,  6,  2,  32, 32, 5,    //  0x39  9
  32, 32, 32, 32, 32, 32,   //  0x3A
  32, 32, 32, 32, 32, 32,   //  0x3B
  32, 32, 32, 32, 32, 32,   //  0x3C
  32, 32, 32, 32, 32, 32,   //  0x3D
  32, 32, 32, 32, 32, 32,   //  0x3E
  1,  6,  2,  254,7,  32,   //  0x3F  ?

  32, 32, 32, 32, 32, 32,   //  0x40  @
  0,  6,  2,  255,254,255,  //  0x41  A
  255,6,  5,  255,7,  2,    //  0x42  B
  0,  1,  1,  3,  4,  4,    //  0x43  C
  255,1,  2,  255,4,  5,    //  0x44  D
  255,6,  6,  255,7,  7,    //  0x45  E
  255,6,  6,  255,32, 32,   //  0x46  F

  0,  1,  1,  3,  4,  2,    //  0x47  G
  255,4,  255,255,254,255,  //  0x48  H
  1,  255,1,  4,  255,4,    //  0x49  I
  32, 32, 255,4,  4,  5,    //  0x4A  J
  255,4,  5,  255,254,2,    //  0x4B  K
  255,32, 32, 255,4,  4,    //  0x4C  L
  32, 32, 32, 32, 32, 32,   //  0x4D  M place holder
  32, 32, 32, 32, 32, 32,   //  0x4E  N place holder
  0,  1,  2,  3,  4,  5,    //  0x4F  O (same as zero)

  0,  6,  2,  3,  32, 32,   //  0x50  P
  32, 32, 32, 32, 32, 32,   //  0x51  Q
  0,  6,  5,  3,  32, 2,    //  0x52  R
  0,  6,  6,  7,  7,  5,    //  0x35  S (same as 5)
  1,  2,  1,  32, 5,  32,   //  0x54  T
  2,  32, 2,  3,  4,  5,    //  0x55  U
  32, 32, 32, 32, 32, 32,   //  0x56  V place holder
  32, 32, 32, 32, 32, 32,   //  0x57  W place holder
  3,  4,  5,  0,  32, 2,    //  0x58  X
  3,  4,  5,  32, 5,  32,   //  0x59  Y
  1,  6,  5,  0,  7,  4,    //  0x5A  Z
  0

};

//* we have a seperate table for the wide routines
const uint8_t gBigFontAsciiTableWide[]  = {
//* this table is 10 bytes, 2 rows of 5
//  ---top------------|
  0,  1,  3,  1,  2,  3,  32, 32, 32, 5,    //  0x4D  M   5-wide
  0,  3,  32, 2,  32, 3,  32, 2,  5,  32,   //  0x4E  N   4-wide
  0,  1,  2,  32, 32, 3,  4,  3,  4,  32,   //  0x51  Q   4-wide
  3,  32, 32, 5,  32, 32, 3,  5,  32, 32,   //  0x56  V   4-wide
  0,  32, 32, 32, 2,  3,  4,  0,  4,  5,    //  0x57  W   5-wide
  0
};


//Setup sensor pin numbers
const uint8_t temp_power_pin = 20; //Set Vcc pins
const uint8_t color_power_pin = 23;
const uint8_t light_power_pin = 17;
const uint8_t color_interrupt_pin = 16; //Set interrupt pins
const uint8_t light_interrupt_pin = 21;
const uint8_t I2C_pullup_pin = 8; //Pin providing I2C pullup voltage
TwoWire* temp_port = &Wire; //Set I2C (wire) ports
TwoWire* color_port = &Wire;
TwoWire* light_port = &Wire1;

//Sensor settings:
const float color_gain_value[] = {1, 4, 16, 60};
const uint8_t color_gain_command[] = {0x00, 0x01, 0x02, 0x03}; 
const uint8_t color_max_index = sizeof(color_gain_value)/sizeof(color_gain_value[0])-1;
uint8_t color_gain_index = color_max_index; //Start at maximum sensitivity
const uint16_t color_integration_value[] = {24, 101, 154, 700};
const uint8_t color_integration_command[] = {0xF6, 0xD5, 0xC0, 0x00};
const uint16_t color_integration_max_count[] = {10240, 43008, 65535, 65535}; //Max ADC count for given integration time 
uint8_t color_integration_index = color_max_index; //Start at maximum sensitivity
const uint8_t color_over_shift = 1; //Over-saturated cutoff - number of shifts to max value (= divide by 2 per shift)
const uint8_t color_under_shift = color_over_shift + 3; //Exposure steps in 2^2 so min is 2 + 1 = >>3 
uint16_t color_over_exposed = color_integration_max_count[color_integration_index] >> color_over_shift;
uint16_t color_under_exposed = color_integration_max_count[color_integration_index] >> color_under_shift;

const float vis_gain_value[] = {1, 24.5, 400, 9200};
const float IR_gain_value[] = {1, 24.5, 400, 9900};
const uint8_t light_gain_command[] = {0x00, 0x10, 0x20, 0x30}; 
const uint8_t light_max_index = sizeof(vis_gain_value)/sizeof(vis_gain_value[0])-1;
uint8_t light_gain_index = light_max_index; //Start at maximum sensitivity
const uint16_t light_integration_value[] = {100, 200, 400, 600};
const uint8_t light_integration_command[] = {0x00, 0x01, 0x03, 0x05};
const uint16_t light_integration_max_count[] = {36863, 65535, 65535, 65535}; //Max ADC count for given integration time 
uint8_t light_integration_index = light_max_index; //Start at maximum sensitivity
const uint8_t light_over_shift = 1; //Over-saturated cutoff - number of shifts to max value (= divide by 2 per shift)
const uint8_t light_under_shift = light_over_shift + 6; //Gain steps in 2^5 so min is 5 + 1 = >>6 
uint16_t light_over_exposed = light_integration_max_count[light_integration_index] >> light_over_shift;
uint16_t light_under_exposed = light_integration_max_count[light_integration_index] >> light_under_shift;

//Setup joystick pins
const uint8_t joystick_pins[] = {9, 6, 2, 7, 4}; //Joystick pins - up, right, down, left, push 
                              //u,  r,  d, l, center 
const uint8_t debounce = 50; //Time in ms to debounce button press

//Setup battery test pin numbers
const uint8_t Vin_test_pin = 11;
const uint8_t Vin_analog_pin = A1; 

//Setup SD card
const int chipSelect = BUILTIN_SDCARD;
Sd2Card card;
SdVolume volume;
SdFile root;
File f;
boolean boot_file_saved = false; //Whether the boot log has been saved to the SD card

//Component status
boolean display_present = false;
boolean display_on = false;
boolean backlight_on = false;
boolean temp_present = false;
boolean temp_on = false;
boolean color_present = false;
boolean color_on = false;
boolean light_present = false;
boolean light_on = false;
boolean SD_present = false;
uint8_t wakeup_source; //Source of wake from hibernate
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

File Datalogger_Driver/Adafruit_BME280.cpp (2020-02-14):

/*!
 * @file Adafruit_BME280.cpp
 *
 * @mainpage Adafruit BME280 humidity, temperature & pressure sensor
 *
 * @section intro_sec Introduction
 *
 *  Driver for the BME280 humidity, temperature & pressure sensor
 *
 * These sensors use I2C or SPI to communicate, 2 or 4 pins are required
 * to interface.
 *
 * Designed specifically to work with the Adafruit BME280 Breakout
 * ----> http://www.adafruit.com/products/2652
 *
 *  Adafruit invests time and resources providing this open source code,
 *  please support Adafruit and open-source hardware by purchasing
 *  products from Adafruit!
 *
 * @section author Author
 *
 * Written by Kevin "KTOWN" Townsend for Adafruit Industries.
 *
 * @section license License
 *
 * BSD license, all text here must be included in any redistribution.
 * See the LICENSE file for details.
 *
 */

#include "Adafruit_BME280.h"
#include "Arduino.h"
#include <SPI.h>
#include <Wire.h>

/*!
 *  @brief  class constructor
 */
Adafruit_BME280::Adafruit_BME280() : _cs(-1), _mosi(-1), _miso(-1), _sck(-1) {}

/*!
 *   @brief  class constructor if using hardware SPI
 *   @param  cspin the chip select pin to use
 *   @param  *theSPI
 *           optional SPI object
 */
Adafruit_BME280::Adafruit_BME280(int8_t cspin, SPIClass *theSPI) {
  _cs = cspin;
  _mosi = _miso = _sck = -1;
  _spi = theSPI;
}

/*!
 *   @brief  class constructor if using software SPI
 *   @param cspin the chip select pin to use
 *   @param mosipin the MOSI pin to use
 *   @param misopin the MISO pin to use
 *   @param sckpin the SCK pin to use
 */
Adafruit_BME280::Adafruit_BME280(int8_t cspin, int8_t mosipin, int8_t misopin,
                                 int8_t sckpin)
    : _cs(cspin), _mosi(mosipin), _miso(misopin), _sck(sckpin) {}

Adafruit_BME280::~Adafruit_BME280(void) {
  if (temp_sensor) {
    delete temp_sensor;
  }
  if (pressure_sensor) {
    delete pressure_sensor;
  }
  if (humidity_sensor) {
    delete humidity_sensor;
  }
}

/*!
 *   @brief  Initialise sensor with given parameters / settings
 *   @param addr the I2C address the device can be found on
 *   @param theWire the I2C object to use, defaults to &Wire
 *   @returns true on success, false otherwise
 */
bool Adafruit_BME280::begin(uint8_t addr, TwoWire *theWire) {
  bool status = false;
  _i2caddr = addr;
  _wire = theWire;
  status = init();

  return status;
}

/*!
 *   @brief  Initialise sensor with given parameters / settings
 *   @returns true on success, false otherwise
 */
bool Adafruit_BME280::init() {
  // init I2C or SPI sensor interface
  if (_cs == -1) {
    // I2C
    _wire->begin();
  } else {
    digitalWrite(_cs, HIGH);
    pinMode(_cs, OUTPUT);
    if (_sck == -1) {
      // hardware SPI
      _spi->begin();
    } else {
      // software SPI
      pinMode(_sck, OUTPUT);
      pinMode(_mosi, OUTPUT);
      pinMode(_miso, INPUT);
    }
  }

  // check if sensor, i.e. the chip ID is correct
  _sensorID = read8(BME280_REGISTER_CHIPID);
  if (_sensorID != 0x60)
    return false;

  // reset the device using soft-reset
  // this makes sure the IIR is off, etc.
  write8(BME280_REGISTER_SOFTRESET, 0xB6);

  // wait for chip to wake up.
  delay(10);

  // if chip is still reading calibration, delay
  while (isReadingCalibration())
    delay(10);

  readCoefficients(); // read trimming parameters, see DS 4.2.2

  setSampling(); // use defaults

  delay(100);

  return true;
}
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

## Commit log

2020-01-10 Changed to smaller bypass caps
    [Light_intensity_data_logger.kicad_pcb, Light_intensity_data_logger.sch]
2020-01-10 Add power switch and Vbat sense
    [Light_intensity_data_logger.sch]
2020-01-11 Add joystick and display
    [Light_intensity_data_logger.sch]
2020-01-15 Add claw headers and initial PCB layout
    [Display with header.FCStd, Light_intensity_data_logger.kicad_pcb, Light_intensity_data_logger.sch, Teensy 35_36 on doublewide header.FCStd]
2020-01-17 Sensors connected in PCB layout
    [Light_intensity_data_logger.kicad_pcb]
2020-01-17 Teensy flipped sensors rewired
    [Light_intensity_data_logger.kicad_pcb, Light_intensity_data_logger.sch]
2020-01-17 All but left monitor wired
    [Light_intensity_data_logger.kicad_pcb, Light_intensity_data_logger.sch]
2020-01-17 Complete routed draft - pass DRC other than courtyard
    [Light_intensity_data_logger.kicad_pcb, Light_intensity_data_logger.sch]
2020-01-17 First draft complete
    [Light_intensity_data_logger.kicad_pcb]
2020-01-17 Vias optimized
    [Light_intensity_data_logger.kicad_pcb]
2020-01-18 License info and annotations added
    [Light_intensity_data_logger.kicad_pcb, Light_intensity_data_logger.sch]
2020-01-18 Removed extra ground trace
    [Light_intensity_data_logger.kicad_pcb]
2020-01-19 Parts numbered in order, courtyards fixed, bigger banana pads
    [Light_intensity_data_logger.kicad_pcb, Light_intensity_data_logger.sch]
2020-01-19 Rewire LED gate to PWM channel
    [Light_intensity_data_logger.kicad_pcb, Light_intensity_data_logger.sch]
2020-01-19 Switch to 1uF caps for sensors per light sensor spec sheet
    [Light_intensity_data_logger.kicad_pcb, Light_intensity_data_logger.sch]
2020-01-19 Gerber files added
    [Light_intensity_data_logger-B_Cu.gbr, Light_intensity_data_logger-B_Mask.gbr, Light_intensity_data_logger-B_Paste.gbr, Light_intensity_data_logger-B_SilkS.gbr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]
2020-01-20 Replace sensor edge cut with NPTH
    [Light_intensity_data_logger.kicad_pcb]
2020-01-20 Ordered version
    [Light_intensity_data_logger-B_Cu.gbl, Light_intensity_data_logger-B_Mask.gbs, Light_intensity_data_logger-B_Paste.gbr, Light_intensity_data_logger-B_SilkS.gbo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]
2020-01-20 Remove extra info from switch BOM
    [Light_intensity_data_logger.sch]
2020-01-22 PCBWay compatible - max PCB dim <100mm
    [Datalogger with Teensy.FCStd, Light_intensity_data_logger-B_Cu.gbl, Light_intensity_data_logger-B_Mask.gbs, Light_intensity_data_logger-B_SilkS.gbo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]
2020-01-23 LCD implemented as tabbed library - contrast pin function working
2020-01-24 Add Adafruit libaries, specify wire port
2020-01-24 Sync to computer time on upload, add sensor system variables
2020-01-24 Changed Strings to char arrays to be compatible with Arduino
2020-01-24 Fully power down LCD and DAC if LCD fails to boot
2020-01-25 Add function to fully disable display to lowest power state
2020-01-25 Add function to disable display to lowest power state
2020-01-28 8-pin display working 4-pin not fully functional - missing characters
2020-01-28 Add timeout to busy check, add disable display, add address to device begin
2020-01-31 4 pin mode working!
    The issue with 4-pin mode is that it is expecting synchronous inputs, and the Teensy is asynchronous. One implementation got all but '0' and '1' to render correctly, while the for loop implementation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
2020-01-31 4-pin LCD option implemented in ino file
2020-01-31 Add Vbat and Vin voltage test
2020-01-31 Revert "Add Vbat and Vin voltage test"
    This reverts commit c4b5c565b3b1f5829fb307e870f01e86cc5f1558.
2020-01-31 Revert "Revert "Add Vbat and Vin voltage test""
    This reverts commit 85e1a66305e13b341a6e999fe05abeda229eac9e.
2020-02-04 Issue with Snooze.h resolved
    Upgrading to Arduino 1.8.11 and Teensyduino 1.50 made it so that the Teensy 3.6 would enter hibernate and not wake.
    Reverting to Arduino 1.8.10 and Teensyduino 1.48 seemed to resolve the issue.
2020-02-05 Using modified LiquidCrystalFast.h for stable 4 pin - add begin() timeout
2020-02-08 Fixed MOSFET issue - improved routing
    Changed LCD to 4-pin only to free up pins
    Routed data lines in clusters to leave open contiguous blocks of pins
    Kept DAC0 line above PCB
    Attached light interrupt to pin 21 - valid hibernate digital line
    Used analog switch to pulse Vbat to DAC,
    Put N-mos on GND side of LED.
    [Light_intensity_data_logger.kicad_pcb, Light_intensity_data_logger.sch]
2020-02-11 Auto gain feature added for light and color sensor
2020-02-12 Add trace resistor between 3v3 and backlight cap for RC filtering
    Trace resistor is 0.181 ohm
    [Light_intensity_data_logger.kicad_pcb]
2020-02-12 This is draft of PCB submitted to PCBWay, logging works!!!
    [Light_intensity_data_logger-B_Cu.gbl, Light_intensity_data_logger-B_Mask.gbs, Light_intensity_data_logger-B_SilkS.gbo, Light_intensity_data_logger-Edge_Cuts.gm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]
2020-02-13 Power management implemented
    Still need to add ability to cut power to sensors on standby
2020-02-14 Many power saving and SD imporovements
    SD loads in blocks of 512 bytes to improve write speed and save power
    Circular log buffer implemented to allow 512 block writes
    SD missing detection and halt with software reset via joystick.
    Digital wakeups logged during button press help with exit log detection
2020-02-14 More optimizations
    Fixed wake during log on button press
    Made so temp is only read once per BME280 reading
    Removed all serial
    Compiler optmization did not change current draw
2020-02-26 Updated pins to new PCB format
2020-02-27 Add pulldown resistor to LCD LED PWM pin
    Add pull down resistor so that the LCD LED with default to off if the pin is in a high impedance state.
    [Light_intensity_data_logger.kicad_pcb, Light_intensity_data_logger.sch]
2020-03-04 Remove Vbat check since when Teensy powered off it drew 360µA
2020-03-04 Remove Vbat check circuit
    [Light_intensity_data_logger.kicad_pcb, Light_intensity_data_logger.sch]
2020-03-07 Re-organize repository
    [Display with header.FCStd, Light_intensity_data_logger-B_Cu.gbl, Light_intensity_data_logger-B_Mask.gbs, Light_intensity_data_logger-B_SilkS.gbo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]
2020-03-07 Move Teensy.lib file
2020-03-07 Add bill of materials
    [Data logger BOM.xlsx]
2020-03-07 Fix bolt equation
    [Data logger BOM.xlsx]
2020-03-07 Add creative commons license for PCB and schematic
2020-03-07 Fix directory typo
    [Display with header.FCStd, Light_intensity_data_logger.kicad_pcb, Light_intensity_data_logger.sch, Teensy 35_36 on doublewide header.FCStd]
2020-03-11 Add sample log files

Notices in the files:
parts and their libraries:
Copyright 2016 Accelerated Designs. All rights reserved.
